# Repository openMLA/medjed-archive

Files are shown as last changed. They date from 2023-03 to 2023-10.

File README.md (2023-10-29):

> [!important]
>
> This repository has been rebased, making prior history unavailable in this repository. This was done as part of a move to a more scalable future for the repository, where CAD files are managed with git-annex and PCB files are in their own submodule. To get rid of the historical bloat the prior history had to be purged. It can still be accessed at [the medjed archive](https://github.com/openMLA/medjed-archive) or upon email request.

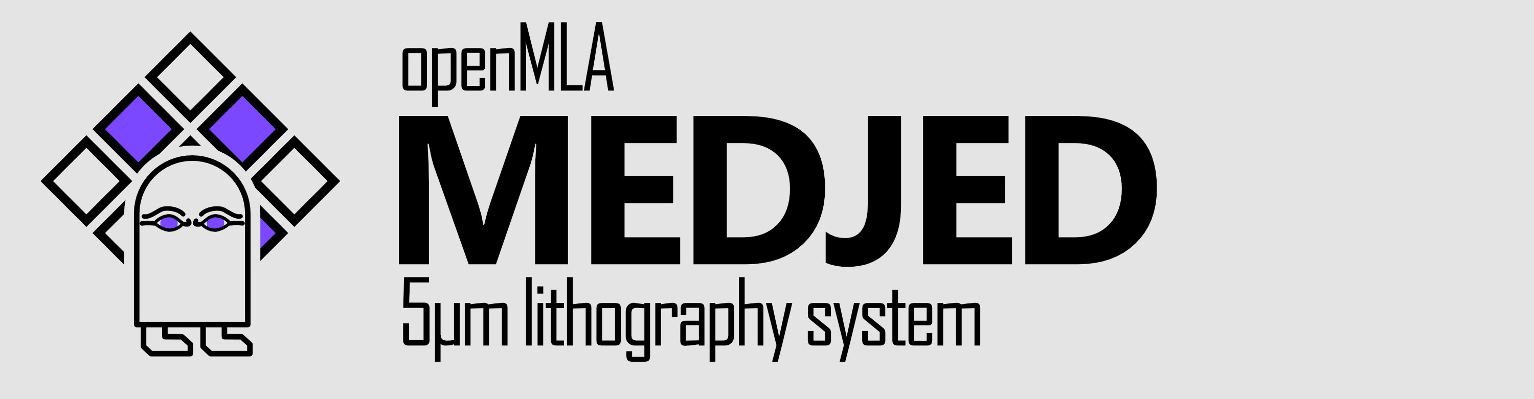
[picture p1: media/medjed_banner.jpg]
medjed_banner


The **Medjed** maskless lithography aligner is part of the openMLA series of photolithography equipment. 

>  **🏗️ Construction in progress**
> A lot is still being worked on for this system. Hardware is being tested and performance will need to be evaluated before people will be able to build their own system. 

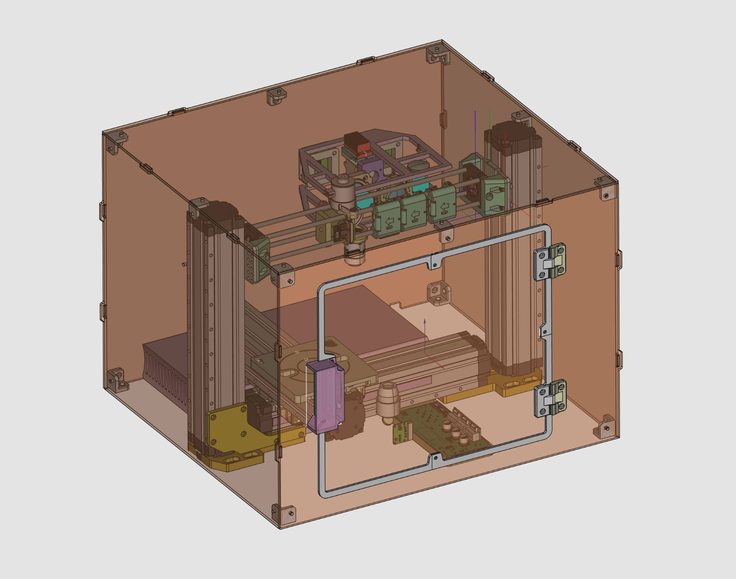
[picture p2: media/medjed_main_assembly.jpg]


### Overview

The MEDJED system is a photolithography system - this means its primary function is to expose a (flat-ish) substrate to patterened light. The substrate will need to be coated in a layer of light-sensitive material known as photoresist. This resist layer in turn will undergo chemical reactions upon exposure to UV light, either rendering areas that were exposed soluble or insoluble to a (liquid) chemical developer. After development of the exposed photoresist layer, some areas of the substrate will remain coated in the photoresist, while others will be free of it. This is the starting point for further patterning steps and is the backbone of modern microfabrication.

The MEDJED system targets a 5um pixel size in its current design. The total project cost is targeted to be 2000-2500 euro. 

There are 3 kinds of documentation for the project:

1. Documentation within this git repository. This is primarily for information about the repository contents.
2. [The project wiki](https://github.com/openMLA/Medjed/wiki). This is for a high level overview of the project, and more in-depth worked out ideas and theory.
3. [The GitHub discussions page](https://github.com/openMLA/Medjed/discussions). This is where small updates, prototypes, and failures are logged. If you have any ideas or comments, you can leave them there! 

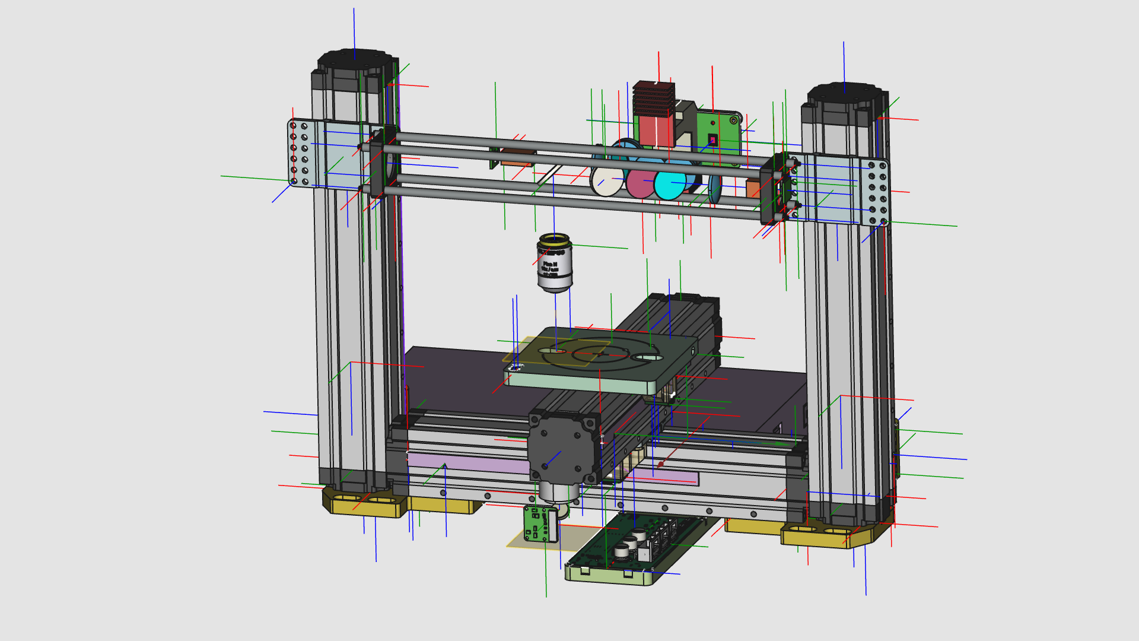
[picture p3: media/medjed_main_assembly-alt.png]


### 🙋‍♂️Contributions

Currently the project development is in volatile waters; a lot is still changing and being tested. If you find the project very interesting and think you have some expertise in the relevant areas (e.g. optics, mechanics, machine safety, PCB design) feel free to reach out so we can see if we can divide up some tasks or if you can share some insight/critique into some of the current design layout!

If you are just interesting in trying out the system, or even just trying out some of the assemblies (e.g. just the Z-axis), your feedback and comments on the design files, practicalities and documentation are also very welcome. You can leave comments and propose new ideas in [the GitHub discussions page](https://github.com/openMLA/Medjed/discussions).

### 📃 Current component selection

Below are some of the current components selected for the machine. They may change at any point and are not necessarily the best for the job.  Still, you may find some of them interesting components for your own project.

🔗 More detailed discussion of components choices will be put in the wiki 📑.

Some highlighted components below

* XYZ axis: Snapmaker linear rails (not accurate enough for direct positioning)
* UV patterning: modified DMD projection unit from the Anycubic Photon Ultra DLP printer. See [this blog post for pictures and background](https://nemoandrea.github.io/blog/Anycubic_DLP_teardown/).
* Main optic: [Olympus Plan N 10X 0.25NA](https://www.edmundoptics.com/f/olympus-plan-achromatic-objectives/14535/).  Alternatively, [a cheaper version with the same optical design is produced in China](https://www.astroshop.eu/for-microscopes/evident-olympus-plcn10x-0-25-plan-achromat-objective/p,49913) by Olympus (part:N4239000) which should work just as well. 
* Encoders: [RLS RLC2IC magnetic encoder](https://www.rls.si/eng/rlc2ic-miniature-linear-and-rotary-pcb-level-incremental-magnetic-encoder) - 244nm spec, 2MHz
* Motion controller IC: [TMC4361A](https://www.trinamic.com/fileadmin/assets/Products/ICs_Documents/TMC4361_Datasheet_Rev3.10.pdf)
* Microcontroller: [Teensy 4.1](https://www.pjrc.com/store/teensy41.html)
* Cameras: Raspberry Pi global shutter and HQ camera

### BOM

Consult the [BOM.csv](BOM.csv) for a  complete-ish list of components (note that it is 🏗). The BOM has optional elements.  This allows construction of cheaper versions of MEDJED if certain features are not needed. Some clarification on what the optional modules correspond to:

* WLM: White Light Module: a white light reflection microscope module that allows for inspection of sample after fabrication (image stitching and such)
* BSA: Back Side Alignment: basic camera and optics that allows for backside alignment of substrates
* EXTRA: Catch-all for nice items to have on the system (extra safety switches or extra visual indicators etc), but are not needed for any new functionality.
* ALT: components that can serve as backup for another, preferred, components in the BOM. 

The main BOM in the repository home is aggregated from subassembly BOM's. So you want to look at the components for a subassembly, simply go to the assembly and open the BOM there. [A simple utility function](utils/bom-merger.py) combines the BOMs.

### 👏 Funding Sources

The project is partially funded by the [Delft Open Hardware organisation](https://www.tudelft.nl/en/open-hardware), and the funding made available to them by the [Delft University of Technology](https://www.tudelft.nl/) for the support of open hardware development. Their support has enabled sourcing of components and has been a big enabling factor for the project development, and the project developers are grateful for their support.

### 🛠 Design Tools

Hardware parts are designed in [FreeCAD](https://www.freecad.org/)

PCBs are designed in [KiCAD](https://www.kicad.org/)

Art/Design is generated by Affinity Designer and [Inkscape](https://inkscape.org/).

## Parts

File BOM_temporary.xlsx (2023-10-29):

Description | Manufacturer part number | Price total | Quantity | Comments
Snapmaker Linear axes 168mm (3 axes per set) |  | 240 | 2 | We only need 4 axes, so we will have 2 spare… | Total Cost
Thorlabs optical cage rods (12") |  | 80.0 | 4 |  | €3109.10
Cage plates standard | CP33/M (https://www.thorlabs.com/thorproduct.cfm?partnumber=CP33/M) | 42.0 | 2
Olympus 10X 0.25Na PlanC N |  | 200 | 1
RLS RL2IC encoders |  | 245.9 | 3
RLS encoder tape |  | 106.2 | 3 | One of tapes will be shorter and hence cheaper
Acrylic Enclosure panels |  | 110 | 1
Snapmaker axis splitter | B.1.H.A.0001-01 | 29.58 | 2 | We need one to strip connectors, and one to mirror Z-axes
Power Module for Snapmaker 2.0 (https://shop.snapmaker.com/products/power-module-for-snapmaker-2-0) |  | 70 | 1 | Internal power supply can be sourced directly for ~ 50 if cost saving needed
Photon Ultra 3D printer with DMD |  | 340 | 1 | Might be hard to source, look around
USB3 colour camera 1/1.8" | MER2-630-60U3C | 191 | 1 | Seem to charge 50 shipping fee, which is a bit much. Could be replaced by Pi HQ camera (50 eur)
deep red camera | SC0926 | 60 | 1 | Rpi global shutter camera
1" enonomy beamsplitter | EBS1 | 82.28 | 2 | maybe need 3 even
1" cold mirror | FM04 | 51.9 | 1
Silver mirror 1" | ME1-P01 | 73.9068 | 2 |  | Cost of white light module
LED board |  | 80 | 2 | coarse estimation | €471.68
Light tunnels |  | 36 | 2 | coarse estimation
Tube lens visible | AC254-080-A | 96.074 | 1 |  | System without white light
Tube lens IR | AC254-080-A | 96.074 | 1 |  | €2637.42
Biconvex lens illumination | LB1757 | 63.3072 | 2 | These are very much pending revision
PCB stage control |  | 100 | 1 | No idea, just putting down some numbers
PCB Z axis and focus |  | 100 | 1 | No idea, just putting down some numbers
PCB stage calibration sensors |  | 40 | 1 | No idea, just putting down some numbers
Printed parts (SLS/MJF) |  | 250 | 1 | No idea, just putting down some numbers
Fine Z-focus system |  | 250 | 1 | No idea, just putting down some numbers
Screws and fittings |  | 50 | 1 | No idea, just putting down some numbers
Stage vacuum | tetra APS 150 |  | 25 | 1 | point of improvement, but not a priority

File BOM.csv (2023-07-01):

Name | Manufacturer | Manufacturer Number | Supplier | Supplier Number | Quantity | Price Total | Optional | Comments
30mm cage plate Metric |  |  | Thorlabs | CP33/M | 2.0 | 42.0
Biconvex lens MARKER/AUTOFOCUS illumination 1" |  |  | Thorlabs | LB1757-A | 1.0 | 45.48 |  | Placeholder
Biconvex lens WLM illumination 1" |  |  | Thorlabs | LB1757-A | 1.0 | 45.48 | WLM | Placeholder. For white light module
Cold mirror 1" |  |  | Thorlabs | FM04 | 1.0 | 51.9
Emergency Off button | IDEC | YW1B-V4E02R | RS components | 168-2546 | 1.0 | 18.48 | EXTRA
Enconomy Beamsplitter 1" |  |  | Thorlabs | EBS1 | 2.0 | 82.0
LED illumination |  |  | Adafruit | 1643 | 1.0 | 9.0 | BSA | Very preliminary pick; may need a simple custom board
LED illumination board MARKER/AUTOFOCUS |  |  | tbd | tbd | 1.0 | 40.0 |  | Placeholder
LED illumination board WLM |  |  | tbd | tbd | 1.0 | 40.0 | WLM | Placeholder. For white light module
Light tunnel MARKER/AUTOFOCUS |  |  | tbd | tbd | 1.0 | 18.0 |  | Placeholder
Light tunnel WLM |  |  | tbd | tbd | 1.0 | 18.0 | WLM | Placeholder. For white light module
M3 heat inserts |  |  | 3DJAKE | ISP-GWEM3 | 4.0 | 5.69 |  | 50 piece set; for vacuum region selection
M4 Inbus bolt 10mm |  |  | Generic | XX001 | 65.0 | 12.5
M4 Inbus nut |  |  | Generic | XX002 | 25.0 | 1.25
M4 Setscrews |  |  | Thorlabs | SS4MS5 | 1.0 | 6.35 |  | pack of 50 setscrews
M4 heat inserts | Ruthex |  | 3DJAKE | RUT-GE-M4x81-001 | 4.0 | 9.5 |  | For attaching stage
M5 heat inserts | Ruthex |  | 3DJAKE | RUT-GE-M5x95-001 | 1.0 | 10.0 |  | For vacuum fitting; pack of 50; ask a friend if they have something like it to save some money
MGN9H linear carriage and 50mm rail |  |  | Fermio.xyz | FLG-MGN-09H-50-SUS | 1.0 | 15.0 |  | Equivalents from other brands (better or cheaper) should work just fine
Motic 10X Objective RedLine200 | Motic | 12220181 | astroshop.be | 567HJ | 1.0 | 39.0 | BSA | Finite conjugate
Olympus 10X PlanC N | Olympus/Evident |  | Astroshop.be | 49913 | 1.0 | 196.0 |  | Alternatively you can get the Japan-made version for ~400; optical design should be identical
Omron Micro Switch | Omron | D2F-01F-D | Mouser | 653-D2F-01F-D | 1.0 | 0.98 |  | For interlock. Also available at RS at MOQ 5
Optical cage rods 6mm |  |  | Thorlabs | ER12 | 4.0 | 80.0
Photon Ultra | Anycubic | 42700000000000.0 | 3dprima | 27344 | 1.0 | 330.0 |  | To salvage DMD unit from
Pi Camera V2.1 noIR | Raspberry Pi | - | Kiwi Electronics | KW-1703 | 1.0 | 28.95 | BSA
Polyimide hinges | Pinet | 54-A-3031 | RS components | 407-6950 | 2.0 | 17.0
RLS encoder RLC2IC |  |  | RLS | RLC2ICA13BB13A00 | 3.0 | 245.85000000000002
RLS magnetic tape 210mm with ref mark |  |  | RLS | MS05DM210AM027 | 2.0 | 70.76
RLS magnetic tape MS - 26mm |  |  | RLS | MS05DM026AM010 | 1.0 | 19.0 |  | 26mm with reference mark at 10mm. Back adhesive pre-applied.
Raspberry Pi global shutter camera | Raspberry Pi |  | Kiwi Electronics | KW-3146 | 1.0 | 60.0 |  | C/CS mount is preferred
Raspberry Pi high quality camera | Raspberry Pi |  | Kiwi Electronics | KW-2906 | 1.0 | 60.0 |  | C/CS mount is preferred
SLS printed parts | fine z-axis |  |  | Vormz.nl |  | 1.0 | 24.0 |  | Price is approximation and might be higher depending on supplier of choice
Silver mirror 1" |  |  | Thorlabs | ME1-P01 | 1.0 | 36.95
Silver mirror WLM 1" |  |  | Thorlabs | ME1-P01 | 1.0 | 36.95 | WLM | For white light module
Small non-captive stepper |  |  | Stepperonline | 28LN24L01-233 | 1.0 | 14.75
Snapmaker axis splitter (converter) | Snapmaker |  | 3D Jake | SM-B.1.H.A.0001-01 | 2.0 | 25.98 |  | Splits step/dir and can bus between two axes (for coarse Z axis)
Snapmaker linear axis 2.0 A150 for X and Y | Snapmaker |  | 123-3D | DAR00374 | 4.0 | 480.0 |  | For now only the 250mm version is available; design is built around the 168mm variant
Snapmaker power supply | Snapmaker |  | 3D Jake | SM-B.1.B.A.0002-01 | 1.0 | 69.0 |  | Price seems to fluctuate; see if you can pick it up for <90 otherwise pick up the internal supply directly (see other entry in BOM)
Tetra APS150 pump | Tetra |  | Amazon.de |  | 1.0 | 17.0 |  | Stage vacuum pump when diaphragm is reversed; point for future improvement
Tube lens DMD 1" 80mm |  |  | Thorlabs | AC254-080-A | 1.0 | 96.07
Tube lens MARKER/AUTOFOCUS 1" 60mm |  |  | Thorlabs | AC254-060-A | 1.0 | 96.07
Tube lens WLM 1" 75mm |  |  | Thorlabs | AC254-075-A | 1.0 | 96.07 | WLM | For white light module
Base Price |  |  |  |  |  | 2279.08
WLM additional cost |  |  |  |  |  | 236.5
EXTRA additional cost |  |  |  |  |  | 18.48
BSA additional cost |  |  |  |  |  | 76.95

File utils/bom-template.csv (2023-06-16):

Name | Manufacturer | Manufacturer Number | Supplier | Supplier Number | Quantity | Price Total | Optional | Comments

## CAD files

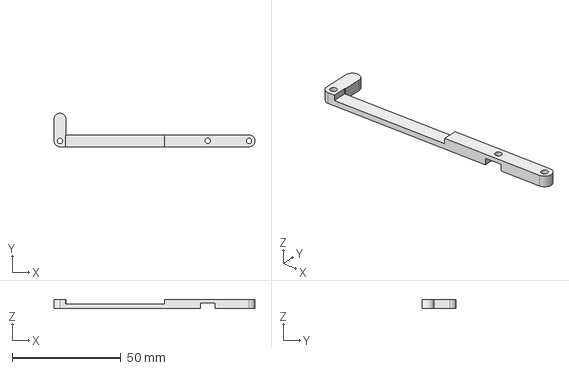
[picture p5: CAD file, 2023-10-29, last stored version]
freeCAD/dev-parts/photon-ultra-lcd-mount/ultra-pcb-combiner-lcd-mainboard.FCStd
92.5 x 15.5 x 4.00 mm

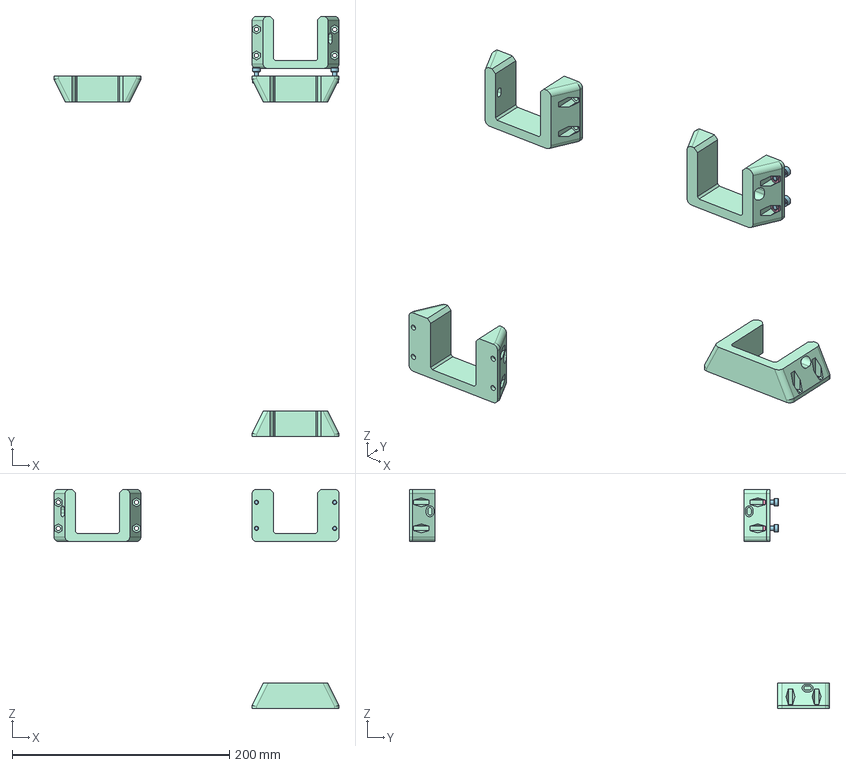
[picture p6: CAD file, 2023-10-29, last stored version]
freeCAD/z-axis-assembly/assembly-z-axis.FCStd
262.4 x 386.9 x 202.0 mm
mounting-bracket x 2
mounting-bracket-mirrored x 2
M4x10-Screw
M4-Nut
M4x10-Screw018
M4x10-Screw019
M4x10-Screw020
M4-Nut017
M4-Nut018
M4-Nut019

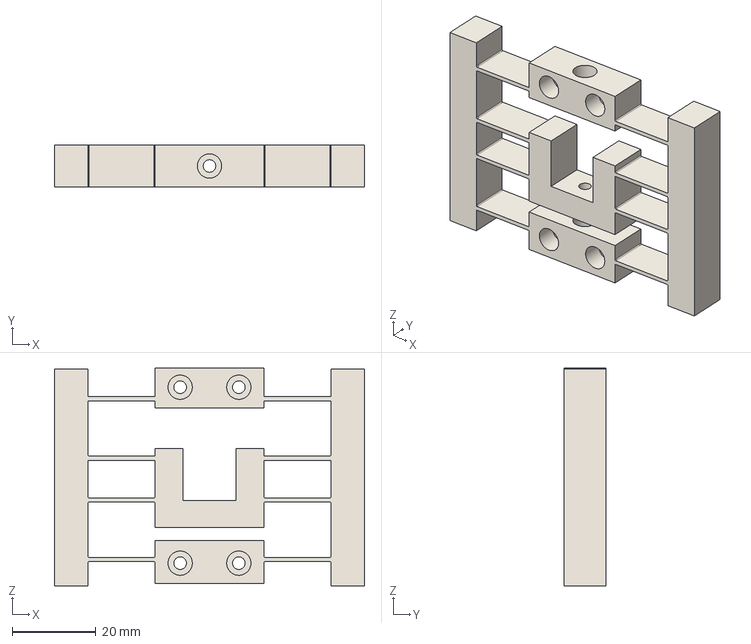
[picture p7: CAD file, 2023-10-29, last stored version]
freeCAD/z-positioner/z-positioner-assembly.FCStd
74.0 x 10.0 x 52.0 mm

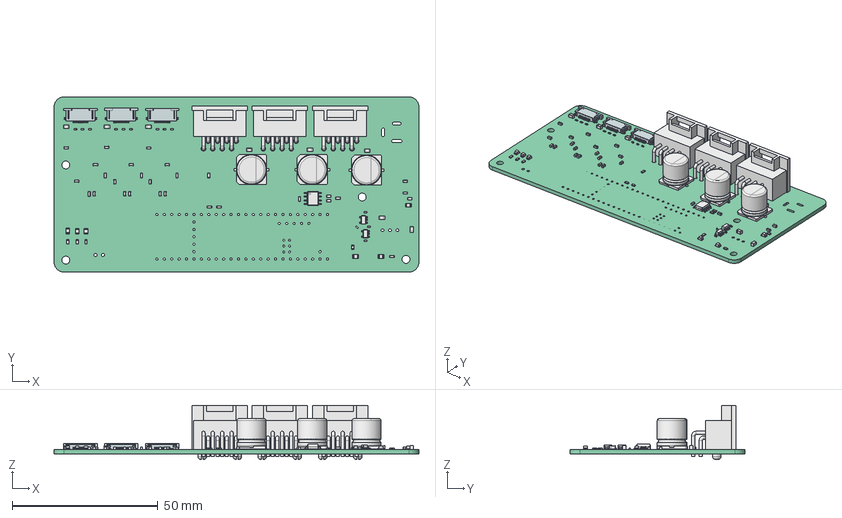
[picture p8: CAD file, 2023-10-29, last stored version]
PCB/stage-controller/freecad-model-mainboard.FCStd
125.0 x 60.0 x 18.5 mm
Pcb_6a43
R4_R_0603_1608Metric_f4cfcd500064 x 11
C1_C_0805_2012Metric_b275aba681d0 x 8
C24_C_0603_1608Metric_a78560b9dbbc x 22
D7_LED_0805_2012Metric_f930eee58cf5 x 6
C15_C_0402_1005Metric_b5bca96c64e8 x 4
U12_SOT_23_5_cb9106183574 x 2
R20_R_0402_1005Metric_df6848926447 x 9
U9_snapmaker_8pin_79d9b302ea48 x 3
C16_CP_Elec_10x105_ca7368eac616 x 3
U6_527451197wbm000_01_160968b98c6b x 3
U10_SOIC_8_39x49mm_P127mm_c27357996c69

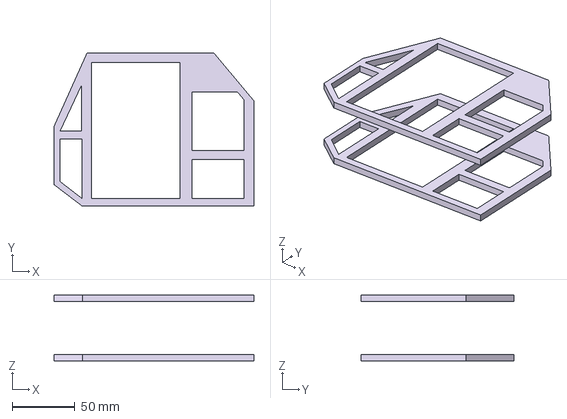
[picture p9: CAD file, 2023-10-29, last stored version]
freeCAD/optics/assembly-optical-medjed.FCStd
158.7 x 121.8 x 52.0 mm
cage-frame x 3

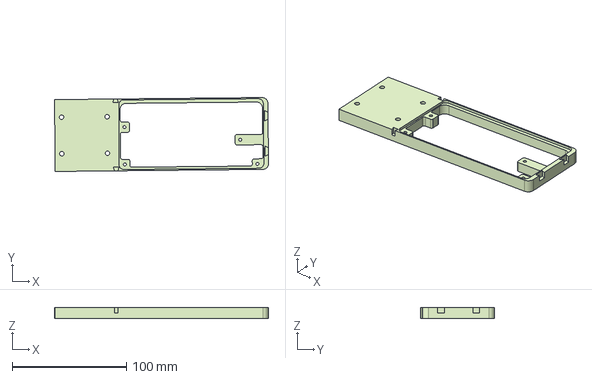
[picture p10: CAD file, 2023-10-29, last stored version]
freeCAD/stage/MainBoard-mount.FCStd
187.6 x 64.8 x 10.0 mm

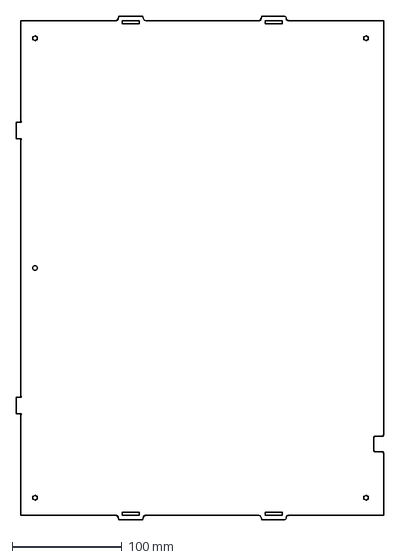
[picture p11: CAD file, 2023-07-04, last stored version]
freeCAD/enclosure/dxf/backpanel.dxf
334.0 x 458.0 mm

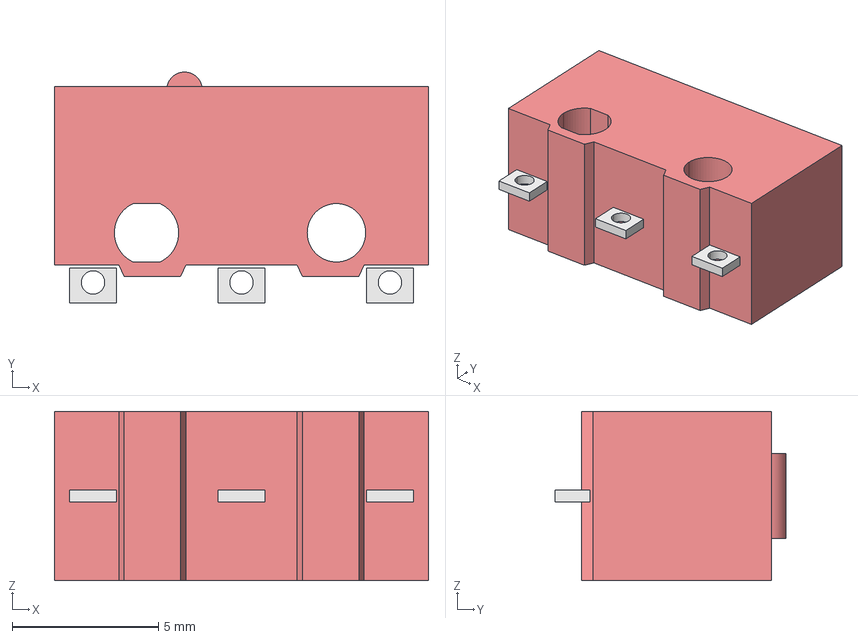
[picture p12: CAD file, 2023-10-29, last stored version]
freeCAD/enclosure/enclosure-door-sensor-omron-D2F.FCStd
12.8 x 7.90 x 5.80 mm
bulk-switch

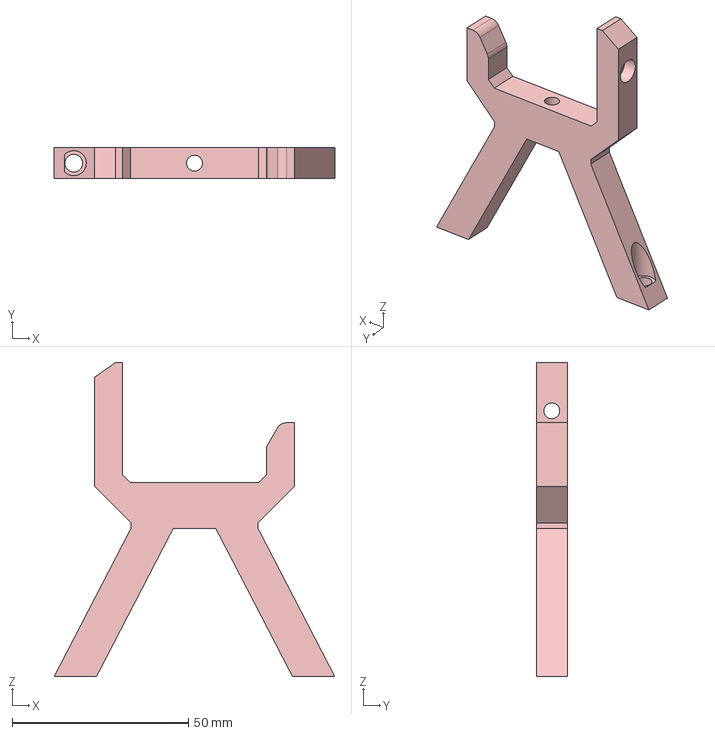
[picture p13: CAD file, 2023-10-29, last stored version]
freeCAD/jigs-and-tools/cage_system_90deg_mounting_stand.FCStd
79.5 x 8.90 x 89.0 mm

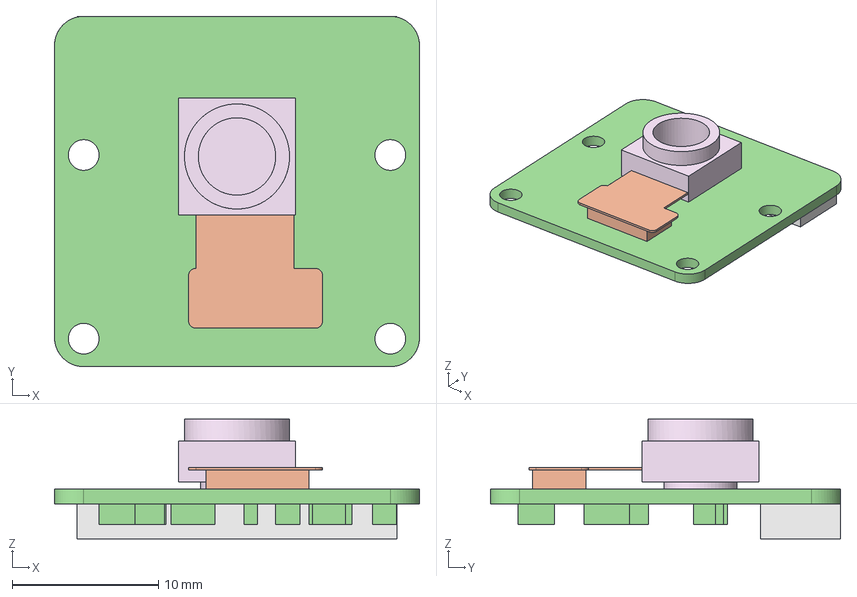
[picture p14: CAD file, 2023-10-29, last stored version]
freeCAD/optics-backside/RPi_camera_V2.1_noIR.FCStd
25.0 x 24.0 x 8.20 mm
RPi_Camera_Module_v2
RPi_Camera_Module_v2001
RPi_Camera_Module_v2003
sensor-no-lens

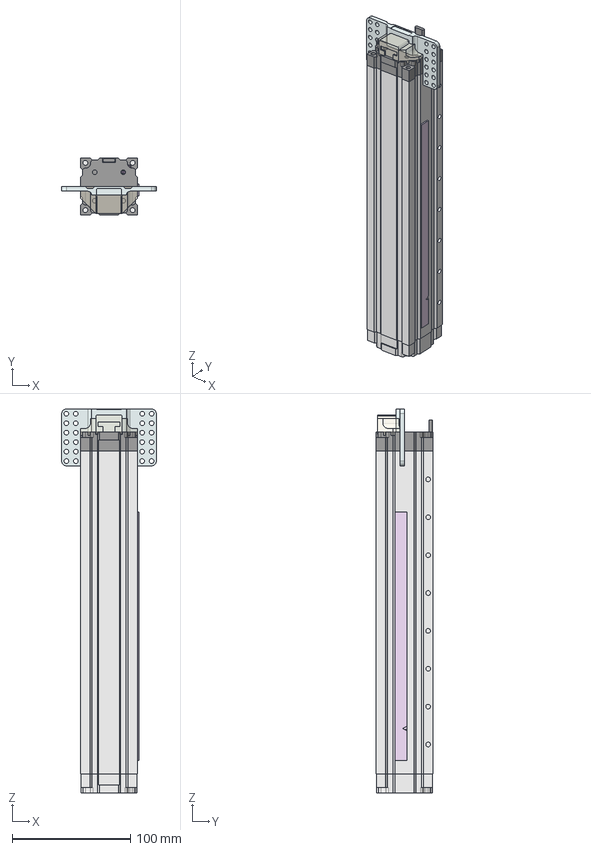
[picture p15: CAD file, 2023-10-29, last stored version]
freeCAD/snapmaker/snapmaker_linear_axis.FCStd
80.0 x 48.2 x 324.5 mm
casing-metal
carriage
endstop-cable
Encoder-tape-210mm
Encoder mounting bracket
Encoder-tape-26mm
Endstop001
RLC2ICAxxxx13Axx

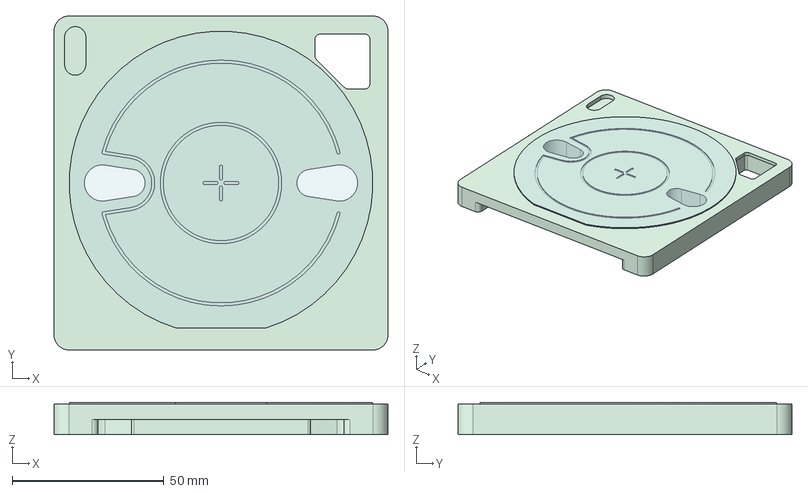
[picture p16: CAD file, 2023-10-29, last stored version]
freeCAD/stage/sample-chuck.FCStd
110.0 x 110.0 x 10.6 mm
sample-chuck
4-inch-wafer

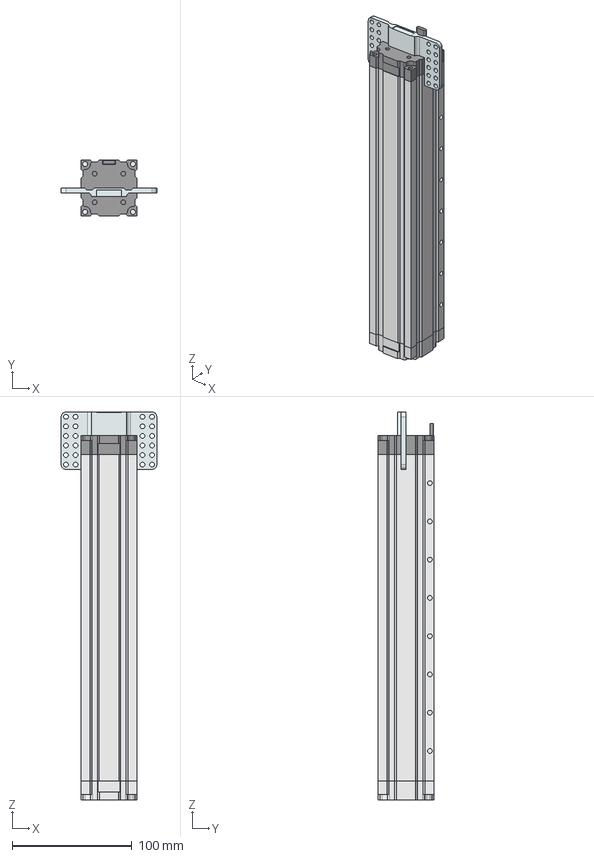
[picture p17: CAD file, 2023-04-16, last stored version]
freeCAD/step_files/snapmaker_linear_axis.FCStd
80.0 x 47.1 x 324.5 mm
casing-metal
carriage
endstop-cable
Endstop001

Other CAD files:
freeCAD/medjed-assembly.FCStd
freeCAD/optics/assembly-optical.FCStd
freeCAD/optics-backside/assembly-backside-optics.FCStd
freeCAD/optics/assembly-optical-stock.FCStd
freeCAD/stage/assembly-stage.FCStd
freeCAD/enclosure/dxf/frontpanel.dxf
freeCAD/enclosure/dxf/sidepanel.dxf
freeCAD/enclosure/dxf/toppanel.dxf
freeCAD/enclosure/enclosure-acrylic.FCStd
freeCAD/enclosure/enclosure-hinges-pinot-40mm.FCStd
freeCAD/jigs-and-tools/backup/rpi-zero-cage-mount_old.FCStd
freeCAD/jigs-and-tools/optics-support-stand.FCStd
freeCAD/jigs-and-tools/rpi-zero-cage-mount.FCStd
freeCAD/optics-backside/objective-motic-PL-4x.FCStd
freeCAD/optics-backside/thorlabs_mirror_ME05-P01.FCStd
freeCAD/optics/45deg_cagebracket.FCStd
freeCAD/optics/Objective_Olympus_PlanN_10X.FCStd
freeCAD/optics/adafruit_LED_pcb_neopixel_jewel.FCStd
freeCAD/optics/backup/OUTDATED_medjed-optics.FCStd
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

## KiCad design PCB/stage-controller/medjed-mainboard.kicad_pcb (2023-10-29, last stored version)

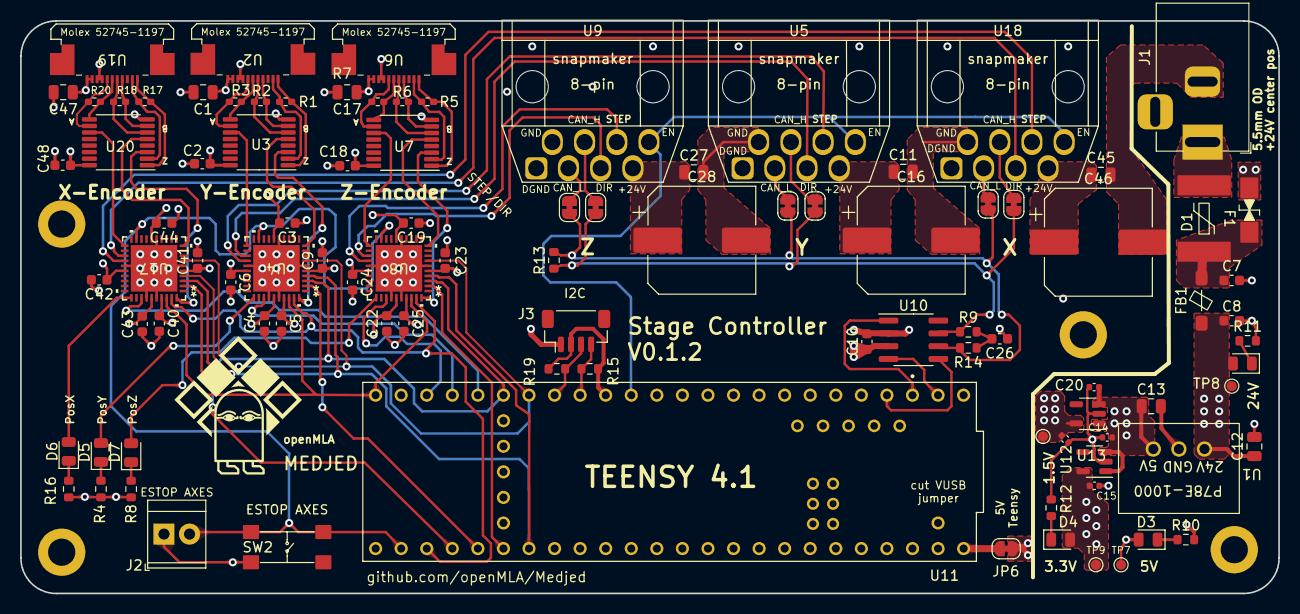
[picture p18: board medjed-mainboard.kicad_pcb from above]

Board: 4 copper layers, 125.0 x 56.9 mm, 98 parts (0 on the bottom side), 78 nets.

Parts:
C1, C11, C12, C17, C27, C45, C47: 10uF; C_0805_2012Metric
C2, C3, C4, C5, C6, C7, C8, C9, C10, C18, C19, C22, C23, C24, C25, C40, C41, C42, C43, C44, C48: 100nF; C_0603_1608Metric
C13: 22uF; C_0805_2012Metric
C14, C15, C20, C21: 1uF; C_0402_1005Metric
C16, C28, C46: 220uF; CP_Elec_220uf
C26: 4.7nF; C_0603_1608Metric
D1: SMAJ28CA
D2, D3, D4, D5, D6, D7: Red; LED_0805_2012Metric
F1: SMDC185F/33-2; SMDC185F_33-2
FB1: FerriteBead; BLM41P600S
J1: Barrel_Jack; BarrelJack_Horizontal
J2: ESTOP terminal; TerminalBlock_TE_282834-2_1x02_P2.54mm_Horizontal
J3: Conn_01x04_Pin; JST_SH_BM04B-SRSS-TB_1x04-1MP_P1.00mm_Vertical
JP1, JP2, JP3, JP4, JP5, JP6, JP7: SolderJumper_2_Bridged; SolderJumper-2_P1.3mm_Bridged_RoundedPad1.0x1.5mm
R1, R2, R3, R5, R6, R7, R17, R18, R20: 120; R_0402_1005Metric_Pad0.72x0.64mm_HandSolder
R4, R8, R10, R11, R12, R15, R16, R19: 5k1; R_0603_1608Metric
R9, R14: 60.4; R_0603_1608Metric
R13: 120; R_0603_1608Metric
SW2: ESTOP switch; E-switch-button
TP7, TP8, TP9, TP10: TestPoint; TestPoint_Pad_D1.0mm
U1: P78E-1000
U2, U6, U19: Molex 52745-1197
U3, U7, U20: TSSOP-16-AM26LS32A
U4, U8, U17: TMC4361A-LA; TMC4361A_QFN40_6X6_TRI
U5, U9, U18: snapmaker_8-pin
U10: TCAN330; SOIC-8_3.9x4.9mm_P1.27mm
U11: teensy 4.1; teensy_4.1
U12: MIC5317-3.3; SOT-23-5
U13: MIC5317-1.8; SOT-23-5

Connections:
+1V8: C3.2, C4.2, C19.2, C21.1, C22.2, C43.2, C44.2, TP10.1, U4.16 (VDD1V8), U4.35 (VDD1V8), U8.16 (VDD1V8), U8.35 (VDD1V8), U13.5 (Vout), U17.16 (VDD1V8), U17.35 (VDD1V8)
+3.3V: C5.1, C6.1, C9.1, C10.1, C15.1, C23.1, C24.1, C25.1, C40.1, C41.1, C42.1, D4.2 (A), TP9.1, U4.5 (VCC), U4.26 (VCC), U4.37 (VCC), U8.5 (VCC), U8.26 (VCC), U8.37 (VCC), U10.3 (VCC), U12.5 (Vout), U17.5 (VCC), U17.26 (VCC), U17.37 (VCC)
+5V: C1.1, C2.1, C13.1, C14.1, C17.1, C18.1, C20.1, C47.1, C48.1, D3.2 (A), JP6.2 (B), TP7.1, U1.3 (Vout), U2.1 (+5V), U2.2 (+5V), U3.16 (Vcc), U6.1 (+5V), U6.2 (+5V), U7.16 (Vcc), U12.1 (Vin), U12.3 (EN), U13.1 (Vin), U13.3 (EN), U19.1 (+5V), U19.2 (+5V), U20.16 (Vcc)
+24V: C8.1, C11.1, C12.1, C16.1, C27.1, C28.1, C45.1, C46.1, D2.2 (A), FB1.2, TP8.1, U1.1 (Vin), U5.7 (+24V), U9.7 (+24V), U18.7 (+24V)
/+3.3V Teensy: J3.2, R15.1, R19.1, U11.3.3V_1 (3.3V), U11.3.3V_2 (3.3V), U11.3.3V_3 (3.3V)
/+24Vfused: C7.1, D1.2 (A2), F1.2, FB1.1
/+24Vsrc: F1.1, J1.1
/Axis X/A: U17.40 (A), U20.3 (1Y)
/Axis X/B: U17.10 (B), U20.5 (2Y)
/Axis X/CAN_H: JP5.1 (A), U18.4 (CAN_H)
/Axis X/CAN_L: JP7.1 (A), U18.3 (CAN_L)
/Axis X/DIR: U17.23 (DIROUT_PWMB), U18.5 (DIR)
/Axis X/N: U17.21 (N), U20.11 (3Y)
/Axis X/STEP: U17.24 (STPOUT_PWMA), U18.6 (STEP)
/Axis X/TGT: D6.2 (A), U17.31 (TARGET_REACHED)
/Axis X/Z_A+: R20.2, U19.5 (A+), U20.10 (3A)
/Axis X/Z_A-: R20.1, U19.6 (A-), U20.9 (3B)
/Axis X/Z_B+: R18.2, U19.7 (B+), U20.6 (2A)
/Axis X/Z_B-: R18.1, U19.8 (B-), U20.7 (2B)
/Axis X/Z_Z+: R17.2, U19.10 (Z+), U20.2 (1A)
/Axis X/Z_Z-: R17.1, U19.11 (Z-), U20.1 (1B)
/Axis Y/A: U3.3 (1Y), U4.40 (A)
/Axis Y/B: U3.5 (2Y), U4.10 (B)
/Axis Y/CAN_H: JP4.1 (A), U5.4 (CAN_H)
/Axis Y/CAN_L: JP3.1 (A), U5.3 (CAN_L)
/Axis Y/DIR: U4.23 (DIROUT_PWMB), U5.5 (DIR)
/Axis Y/N: U3.11 (3Y), U4.21 (N)
/Axis Y/STEP: U4.24 (STPOUT_PWMA), U5.6 (STEP)
/Axis Y/TGT: D5.2 (A), U4.31 (TARGET_REACHED)
/Axis Y/Z_A+: R3.2, U2.5 (A+), U3.10 (3A)
/Axis Y/Z_A-: R3.1, U2.6 (A-), U3.9 (3B)
/Axis Y/Z_B+: R2.2, U2.7 (B+), U3.6 (2A)
/Axis Y/Z_B-: R2.1, U2.8 (B-), U3.7 (2B)
/Axis Y/Z_Z+: R1.2, U2.10 (Z+), U3.2 (1A)
/Axis Y/Z_Z-: R1.1, U2.11 (Z-), U3.1 (1B)
/Axis Z/A: U7.3 (1Y), U8.40 (A)
/Axis Z/B: U7.5 (2Y), U8.10 (B)
/Axis Z/CAN_H: JP1.1 (A), U9.4 (CAN_H)
/Axis Z/CAN_L: JP2.1 (A), U9.3 (CAN_L)
/Axis Z/DIR: U8.23 (DIROUT_PWMB), U9.5 (DIR)
/Axis Z/N: U7.11 (3Y), U8.21 (N)
/Axis Z/STEP: U8.24 (STPOUT_PWMA), U9.6 (STEP)
/Axis Z/TGT: D7.2 (A), U8.31 (TARGET_REACHED)
/Axis Z/Z_A+: R7.2, U6.5 (A+), U7.10 (3A)
/Axis Z/Z_A-: R7.1, U6.6 (A-), U7.9 (3B)
/Axis Z/Z_B+: R6.2, U6.7 (B+), U7.6 (2A)
/Axis Z/Z_B-: R6.1, U6.8 (B-), U7.7 (2B)
/Axis Z/Z_Z+: R5.2, U6.10 (Z+), U7.2 (1A)
/Axis Z/Z_Z-: R5.1, U6.11 (Z-), U7.1 (1B)
/SCL: J3.4, R15.2, U11.24 (A10)
/SDA: J3.3, R19.2, U11.25 (A11)
CAN_EN: U10.5 (SHDN), U11.2 (OUT2)
CAN_H: JP1.2 (B), JP4.2 (B), JP5.2 (B), R9.1, R13.1, U10.7 (CANH)
CAN_L: JP2.2 (B), JP3.2 (B), JP7.2 (B), R13.2, R14.2, U10.6 (CANL)
CS_X: U11.36 (CS2), U17.2 (NSCSIN)
CS_Y: U4.2 (NSCSIN), U11.37 (CS3)
CS_Z: U8.2 (NSCSIN), U11.38 (A14)
EN_SNAP: U5.8 (EN), U9.8 (EN), U11.12 (MISO), U18.8 (EN)
ESTOP: J2.2, SW2.3 (K), SW2.4 (A), U4.19 (NFREEZE), U8.19 (NFREEZE), U11.34 (RX8), U17.19 (NFREEZE)
GND: C1.2, C2.2, C3.1, C4.1, C5.2, C6.2, C7.2, C8.2, C9.2, C10.2, C11.2, C12.2, C13.2, C14.2, C15.2, C16.2, C17.2, C18.2, C19.1, C20.2, C21.2, C22.1, C23.2, C24.2, C25.2, C26.1, C27.2, C28.2, C40.2, C41.2, C42.2, C43.1, C44.1, C45.2, C46.2, C47.2, C48.2, D1.1 (A1), J1.2, J2.1, J3.1, R4.2, R8.2, R10.2, R11.2, R12.2, R16.2, SW2.1, U1.2 (GND), U2.3 (GND), U2.4 (GND), U3.8 (GND), U4.6 (GND), U4.15 (GND), U4.25 (GND), U4.34 (TEST_MODE), U4.36 (GND), U4.41 (GND), U5.1 (DGND), U5.2 (GND), U6.3 (GND), U6.4 (GND), U7.8 (GND), U8.6 (GND), U8.15 (GND), U8.25 (GND), U8.34 (TEST_MODE), U8.36 (GND), U8.41 (GND), U9.1 (DGND), U9.2 (GND), U10.2 (GND), U11.GND1 (GND), U11.GND2 (GND), U11.GND3 (GND), U11.GND4 (GND), U11.GND5 (GND), U12.2 (GND), U13.2 (GND), U17.6 (GND), U17.15 (GND), U17.25 (GND), U17.34 (TEST_MODE), U17.36 (GND), U17.41 (GND), U18.1 (DGND), U18.2 (GND), U19.3 (GND), U19.4 (GND), U20.8 (GND)
INT_X: U11.28 (RX7), U17.33 (INTR)
INT_Y: U4.33 (INTR), U11.29 (TX7)
INT_Z: U8.33 (INTR), U11.30 (CRX3)
MISO: U4.4 (SDIIN), U8.4 (SDIIN), U11.39 (A15), U17.4 (SDIIN)
MOSI: U4.7 (SDOIN), U8.7 (SDOIN), U11.26 (A12), U17.7 (SDOIN)
unnamed: C26.2, R9.2, R14.1
unnamed: D2.1 (K), R11.1
unnamed: D3.1 (K), R10.1
unnamed: D4.1 (K), R12.1
unnamed: D5.1 (K), R4.1
unnamed: D6.1 (K), R16.1
unnamed: D7.1 (K), R8.1
unnamed: JP6.1 (A), U11.VIN
unnamed: U10.4 (RXD), U11.0 (RX1)
unnamed: U10.1 (TXD), U11.1 (TX1)
RST_AXES: U4.39 (NRST), U8.39 (NRST), U11.35 (TX8), U17.39 (NRST)
SCK: U4.3 (SCKIN), U8.3 (SCKIN), U11.27 (A13), U17.3 (SCKIN)
TeensyCLK: U4.38 (CLK_EXT), U8.38 (CLK_EXT), U11.32 (OUT1B), U17.38 (CLK_EXT)

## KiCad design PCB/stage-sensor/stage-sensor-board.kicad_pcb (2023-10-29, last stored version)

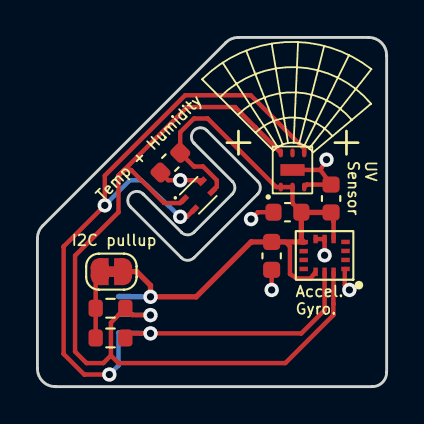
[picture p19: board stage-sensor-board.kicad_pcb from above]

Board: 2 copper layers, 19.4 x 19.4 mm, 11 parts (1 on the bottom side), 5 nets.

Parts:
C3: 10nF; C_0603_1608Metric
C4: 2.2uF; C_0603_1608Metric
C5, C6: 100nF; C_0603_1608Metric
J1: STEMMA QT; JST_SH_BM04B-SRSS-TB_1x04-1MP_P1.00mm_Vertical
JP1: Bridged; SolderJumper-2_P1.3mm_Bridged_RoundedPad1.0x1.5mm
R1, R2: 11K; R_0603_1608Metric
U1: ICM 42605; icm-42605
U2: OPT3002
U3: SHT45; SHT4X

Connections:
+3.3V: C3.1, C4.1, C5.2, C6.2, J1.2, JP1.2 (B), U1.5 (VDDIO), U1.8 (VDD), U1.12 (AP_CS), U2.1 (VDD), U2.2 (ADDR), U3.3 (VDD)
/I2C_pullup: JP1.1 (A), R1.1, R2.1
/SCL: J1.4, R2.2, U1.13 (SCL), U2.4 (SCL), U3.2 (SCL)
/SDA: J1.3, R1.2, U1.14 (SDA), U2.6 (SDA), U3.1 (SDA)
GND: C3.2, C4.2, C5.1, C6.1, J1.1, U1.1 (I2C_addr), U1.6 (GND), U1.7 (GND), U2.3 (GND), U3.4 (VSS)

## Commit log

2023-03-11 Initial documentation
    Add initial documentation and some basic freeCAD files as a sample.
    [crossbrace_snapmaker.FCStd, stage.FCStd]
2023-04-07 Stage controller PCB schematic
    Add most of the components for the stage controller in place. Nothing routed up yet, only working on the schematic and footprints.
    [medjed-mainboard.kicad_pcb, medjed-mainboard.kicad_sch]
2023-04-16 Update freecad files with assemblies
    Add new parts and combine existing parts with assembly 4 workbench in FreeCAD
    [DLP-board-brace.FCStd, assembly-stage.FCStd, assembly-z-axis.FCStd, crossbrace_snapmaker.FCStd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]
2023-04-29 Add initial version stage PCB
    Will probably need major revisions as efforts towards TMC4361A will require significant changes.
    [medjed-mainboard.kicad_pcb, medjed-mainboard.kicad_sch]
2023-04-29 Update stage-PCB schematic
2023-05-06 New TMC4361 design
    Redesigned stage controller around the TMC4361.
    [enc_axis.kicad_sch, medjed-mainboard.kicad_pcb, medjed-mainboard.kicad_sch]
2023-05-07 Finalise part numbers and I2C pullup
    Complete mouser part numbers. Added pullup for I2C connector.
    [enc_axis.kicad_sch, medjed-mainboard.kicad_pcb, medjed-mainboard.kicad_sch]
2023-05-21 Add enclosure files
    Add initial design for an enclosure for the the Medjed system. More work is needed for the main door and interlock.
    [enclosure-acrylic.FCStd]
2023-05-21 stage controller PCB version 0.1.2
    Versino of stage controller produced by Aisler pending testing. Added some 3D models for board visualisation.
    [freecad-model-mainboard.FCStd, medjed-mainboard.kicad_pcb]
2023-05-27 Near Final Enclosure design
    Added door and printed parts design for enclosure. Will need verification by building and cable routing through printed skirting.
    [enclosure-acrylic.FCStd, enclosure-door-sensor-omron-D2F.FCStd, enclosure-hinges-pinot-40mm.FCStd]
2023-05-27 Fix image
    Fixed image for enclosure documentation
2023-05-29 Add early optical design
    [Objective_Olympus_PlanN_10X.FCStd, assembly-optical-medjed.FCStd, assembly-optical-stock.FCStd, assembly-optical.FCStd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]
2023-06-13 Update enclosure for new double-z layout
    Updated enclosure for the new double z axis layout. Functionally still identical.
    [enclosure-acrylic.FCStd, enclosure-hinges-pinot-40mm.FCStd]
2023-06-13 Reorganisation and new assembly images
    Not all files are pushed yet to keep the repository size in check, but new preview of the design is present in the main readme.
    [medjed-assembly.FCStd, snapmaker_linear_axis.FCStd, snapmaker_psu.FCStd]
2023-06-15 Add bom-merger utility
    Simple utility to allow BOMs to be split up between subassemblies. Added two quick demo CSV files to drive the idea home.
    [BOM-subassembly.csv, bom-template.csv]
2023-06-16 Add subassembly BOMs and update utility
    Filled in the BOMs for subassemblies and improved the bom-merger utilities with more capabilities such as optional categories and template filtering.
    [BOM-backside-camera.csv, BOM-optics.csv, BOM-snapmaker-extras.csv, BOM-stage.csv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]
2023-07-01 Add designs for linear-rail+stepper Z-axis
    new Z-axis for focussing.
    [Objective_Olympus_PlanN_10X.FCStd, fermio_MGN9H_linear_rail.FCStd, noncaptive_stepper_28LN24L01-223.FCStd]
2023-07-01 Update BOMs with Z-focus assembly
    [BOM-z-fine-positioner.csv, BOM.csv]
2023-07-04 Update enclosure with print-in-place hinges
    Cleaned up directory and added dxf for for easy ordering.
    [backpanel.dxf, enclosure-acrylic.FCStd, frontpanel.dxf, sidepanel.dxf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]
2023-09-18 Reorganise the sample stage and update design
    Renamed the sample chuck to be more descriptive. Revising the design to be more compact and for resin printing.
    [assembly-stage.FCStd, sample-chuck.FCStd, stage.FCStd]
2023-09-24 Add basic 45 degree cage mount optic holder
    Basic design that complements the tip-tilt holder for basic designs and prototyping
2023-09-24 Add linear rail based z-positioner
    Added designs and basic documentation for a linear-rail based z focus mechanism.
    [z-positioner-linear-rail.FCStd]
2023-09-24 Fix: add freecad file for 45 deg cage bracket
    Forgot to include the freecad file for commit f51dc9b. Did some housekeeping and removed old files that are no longer relevant.
    [45deg_cagebracket.FCStd, thorlabs_C4W_cage.FCStd, z-positioner-linear-rail.FCStd]
2023-09-24 Add sample chuck PCB
    Design files for a new PCB that sits inside the sample chuck. New sample chuck design not yet commited.
    [pcb-sample-chuck.FCStd, stage-sensor-board.kicad_pcb, stage-sensor-board.kicad_sch]
2023-10-07 Add inline tip-tilt design
    New cage element, a 1-inch tip-tilt lens holder. Prototype discussed in https://github.com/openMLA/Medjed/discussions/14
    [thorlabs_AC254-080-A_lens_doublet_f80mm.FCStd, thorlabs_AC554-080-A_lens_doublet_f80mm.FCStd]
2023-10-21 Update main assembly image
    Update the current assembly image with new optical developments.
2023-10-28 Add submodule: assembly
    Add the git-annex managed assembly files as a submodule
2023-10-28 Prepare PCB for submodule mode
2023-10-28 Update assembly submodule version
    Important version bump
2023-10-29 Update PCB files
    Pre-removal and submodule reorganisation
    [enc_axis.kicad_sch, freecad-model-mainboard.FCStd, medjed-mainboard.kicad_pcb, medjed-mainboard.kicad_sch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]
2023-10-29 Remove PCB directory
    In preparatiof of submodule introduction
    [enc_axis.kicad_sch, freecad-model-mainboard.FCStd, medjed-mainboard.kicad_pcb, medjed-mainboard.kicad_sch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]
2023-10-29 Add PCB back as submodule
    Return of the PCB directory but now as a submodule.
2023-10-29 Add final freecad files to clean up directory
    Prior to removal
    [45deg_cagebracket.FCStd, BOM-optics.csv, BOM_temporary.xlsx, MainBoard-mount.FCStd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]
2023-10-29 Remove freecad files from directory
    Will rebase directory in the future to remove this bloat. Files can still be found in submodule.
    [45deg_cagebracket.FCStd, BOM-backside-camera.csv, BOM-optics.csv, BOM-snapmaker-extras.csv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]
